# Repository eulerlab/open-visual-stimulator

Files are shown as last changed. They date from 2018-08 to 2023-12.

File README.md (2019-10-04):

## Open Visual Stimulator

This repository holds the resources for a flexible, spatial visual stimulator with up to 6 chromatic channels. It combines commercial digital light processing (DLP) devices with open hard- and software components that can be easily adapted to the experimentalist’s specific needs. With this we intend to start a community effort of sharing and further developing a common stimulator design.

Please find more details on the stimulator in the following publication:

_Franke K*, Maia Chagas A*, Zhao Z, Zimmermann MJY, Bartel P, Qiu Y, Szatko K, Baden T, Euler T# (2019). An arbitrary-spectrum spatial visual stimulator for vision research. eLife 2019;8:e48779, [10.7554/eLife.48779](https://elifesciences.org/articles/48779)._

For the newest changes and additions, see [release notes](https://github.com/eulerlab/open-visual-stimulator/blob/master/release_notes.md)

### Pictures

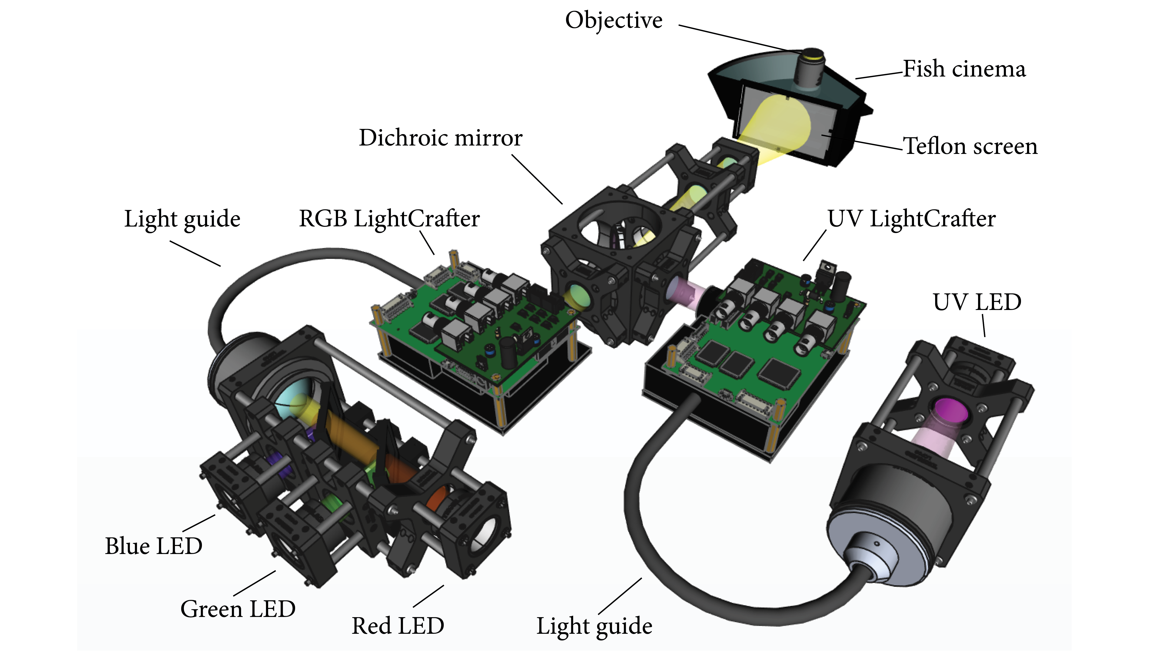
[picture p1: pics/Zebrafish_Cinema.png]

_Rendering of the 4-channel R-G-B-UV zebrafish stimulator (by MJY Zimmermann)._

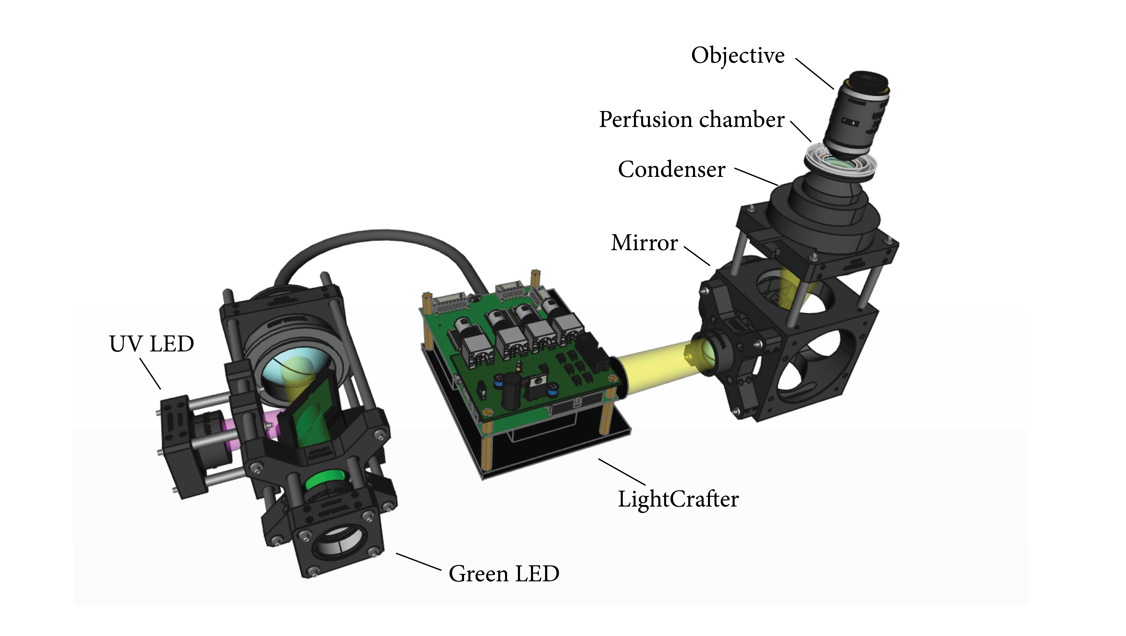
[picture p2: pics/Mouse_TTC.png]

_Rendering of through-the-conderser (TTC) G-UV mouse light stimulator (by MJY Zimmermann)._

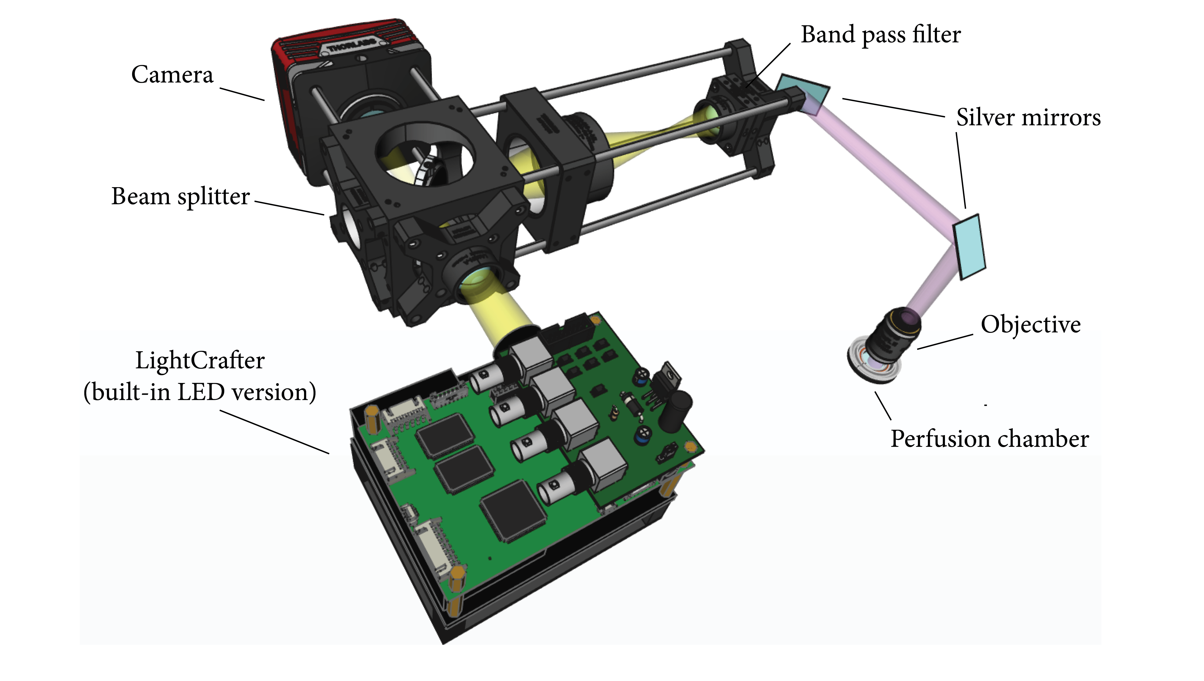
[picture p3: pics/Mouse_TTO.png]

_Rendering of through-the-objective (TTO) G-UV mouse light stimulator (by MJY Zimmermann)._ 

### Ordering of PCB boards

If you are interested in ordering boards and components, please find more information in the boards folder [readme](https://github.com/eulerlab/open-visual-stimulator/blob/master/boards/readme.md) file.

## Repository structure

```
├───pics                                      Pictures
├───boards                                    LED driver/blanking boards
│   ├───lcr_add-on                            - KiCad files for board that combines LCr and
|   |   |                                       blanking signals
|   |   ├───connector_coaxial.pretty          - BNC connector description (KiCad)
|   |   └───gerber                            - Gerber files for circuit board
│   ├───mosfet_circuit                        - KiCad files for board that switches switch LEDs
|   |   ├───connector_coaxial.pretty          - BNC connector description (KiCad)
|   |   └───gerber                            - Gerber files for circuit board
|   ├───mosfet_circuit_plus_voltage_regulator - KiCad files for board that combines voltage
|   |   |                                       regulator and LED switching
|   |   ├───connector_coaxial.pretty          - BNC connector description (KiCad)
|   |   └───gerbers                           - Gerber files for circuit board
|   ├───ssr_board                             - KiCad files for solid state relay board
|   |   └───gerbers                           - Gerber files for circuit board
|   └───arduino_code_for_testing_circuits     - Arduino code to emulate blanking and LCr signals
|       └───lcr_emulator
|
├───printed_parts                             OpenSCAD and STL files for 3D printed parts
|   |
│   ├───Fish_cinema                           - Fish tank used in the fish setup
│   ├───SSR_board                             - Designs for plate and cover of the SSR board
│   └───optical_components                    - optomechanical parts for LED assemblies
|           ├───fish_stimulator
|           ├───cmouse_stimulator
|           └───lcr_addons
├───calibration_mouse                         Calibration of dichroic mouse stimulator
│   ├───data                                  - recorded calibration data (custom LEDs and TFT monitor)
│   ├───datasheets                            - spectrometer data sheet, etc.
│   ├───filters                               - dichroic filter spectra
│   ├───light-sources                         - spectra of LEDs
│   ├───opsins                                - mouse opsin sensitivity curves
│   ├───scripts                               - Python scripts used in iPython notebooks
|   └───spectrometer-calibration-files        - USB2+ calibration data
|
└───calibration_zebrafish                     Calibration of tetrachromatic zebrafish stimulator
    ├───data                                  - recorded calibration data (custom LEDs)
    ├───datasheets                            - spectrometer & powermeter data sheet.
    ├───light-sources                         - LED spectra measured behind the teflon screen
    ├───opsins                                - zebrafish opsin sensitivity curves
    └───scripts                               - Python scripts used in iPython notebooks
```

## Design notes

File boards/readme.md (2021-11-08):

## LED driver/blanking boards

LED blanking circuits were inspired by earlier devices designed and built by R. Berndt (HIH Tübingen).

`lcr_add-on` - KiCad and Gerber files for the "logic board". This board combines the signals from the LCr with an external "blanking signal" to independently control up to three 3 LEDs per lightcrafter device. This board has a jumper option to disable the blanking signal altogether, which may be useful when e.g. using LCrs in MEA setups.

`mosfet_circuit` - KiCad and Gerber files for "LED driver board". This board uses the 5V logic signal from Lcr_addon ("logic board") to turn LEDs on and off. Users need to connect this board to an appropriate power suply (i.e. a power supply the is outputing the LED forward voltage).

`mosfet_circuit_plus_voltage_regulator` - KiCad and Gerber files for "LED driver board". This board uses the 5V logic signal from Lcr_addon ("logic board") to turn LEDs on and off. This board has a stepdown voltage regulator built-in. It is capable of 20V and 1.5A max output with the components present in its "1-click-bom.csv" file. (see "Components to populate the boards" for more details).

`ssr_board` - This board controls the LED power lines from the Lightcrafter by opening and closing them using solid state relays. The relays are controlled by a 5V signal (in this case the inverted blanking signal).

### General information about the printed circuit boards:

- For details on the design and function of the boards, see [preprint](https://www.biorxiv.org/content/10.1101/649566v1)).

- The boards were designed using [KiCad 5](http://www.kicad.org/) and can be ordered using the `Gerber.zip` file located in each board's `gerber` subfolder.

- Several "board on demand" companies are available, and the process of ordering is pretty much the same. A more detailed tutorial on how to do so can be found [here](https://www.youtube.com/watch?v=ENmDnoKs2hM) (for simply using the already available compressed files, go to minute 7 of the video).

- Companies providing "board on demand" service include:

   - [JLCPCB](https://jlcpcb.com/)
   - [PCBWAY](https://www.pcbway.com)
   - [OSH PARK](https://oshpark.com/)
   - [AISLER](https://aisler.net/)

### Components to populate the boards:

Components are listed on each board folder on a "comma separated value" file named `1-click-bom.csv`. Listed in the file are the quantity, identification and supplier of each component. They can also be ordered using [KitSpace](kitspace.org):

 - [LCr_addon on kitspace](https://kitspace.org/boards/github.com/eulerlab/open-visual-stimulator/boards/lcr_add-on/)
 - [mosfet circuit on kitspace](https://kitspace.org/boards/github.com/eulerlab/open-visual-stimulator/boards/mosfet_circuit/)
 - [mosfet  plus voltage regulator circuit on kitspace](https://kitspace.org/boards/github.com/eulerlab/open-visual-stimulator/boards/mosfet_circuit_plus_voltage_regulator/)

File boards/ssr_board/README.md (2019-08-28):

# Open Visual Stimulator - Solid State relay board

This board controls the LED power lines from the Lightcrafter by opening and closing them using solid state relays. The relays are controlled by a 5V signal (in this case the inverted blanking signal).

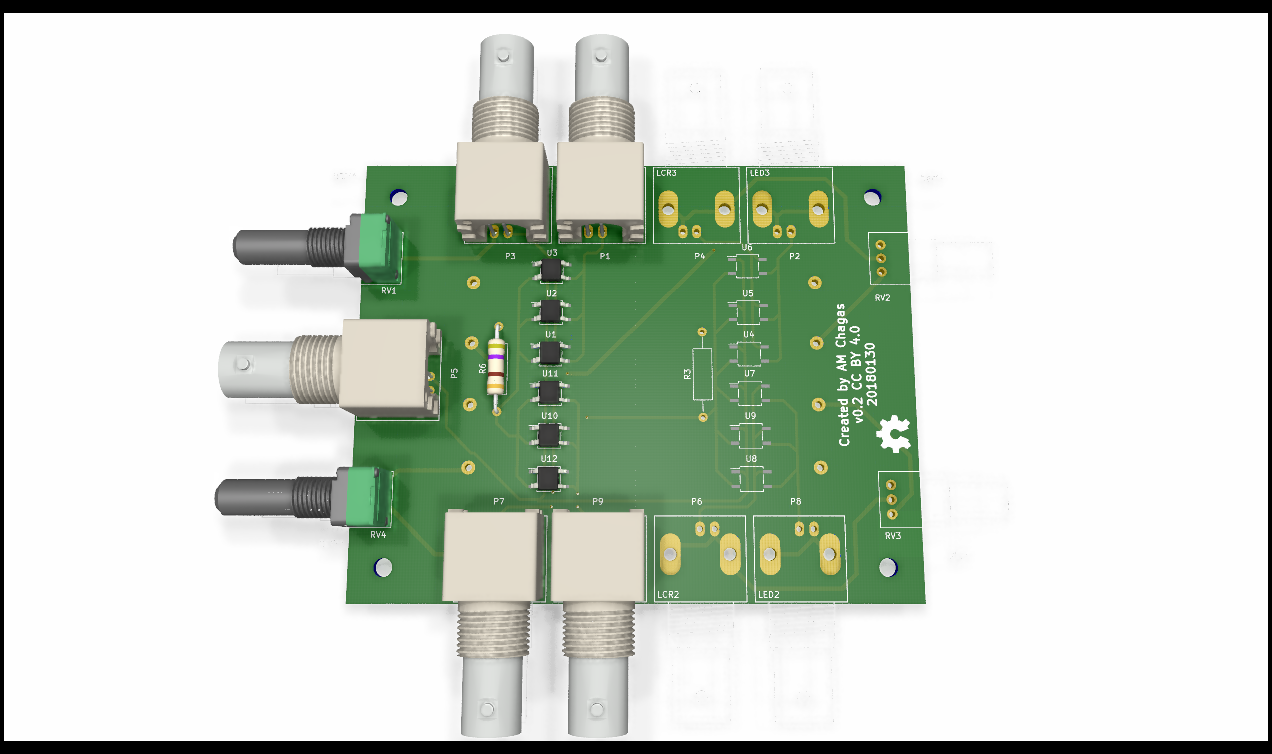
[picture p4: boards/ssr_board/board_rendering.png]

rendering for two out of four possible channels.

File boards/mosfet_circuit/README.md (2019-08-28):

# Open Visual Stimulator - MOSFET Circuit PCB

A board ("LED driver board") for fast switching LEDs on/off, part of the Open Source visual stimulator project.

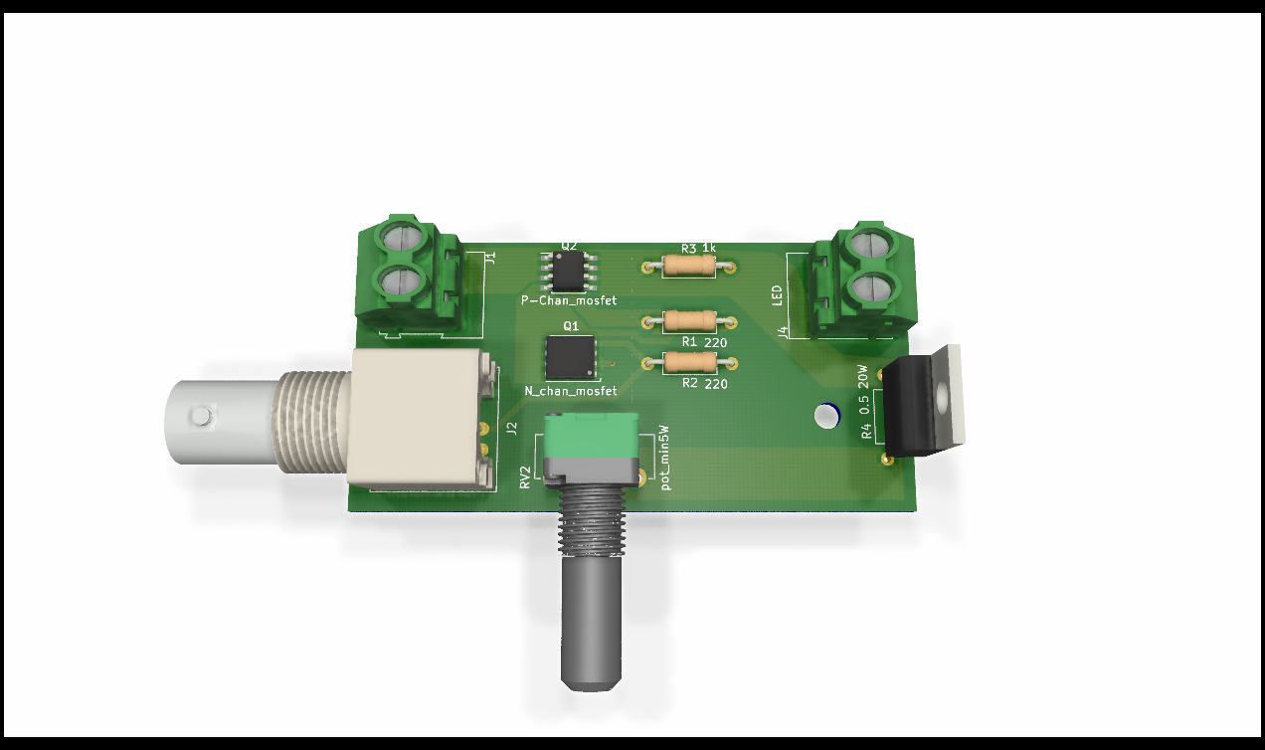
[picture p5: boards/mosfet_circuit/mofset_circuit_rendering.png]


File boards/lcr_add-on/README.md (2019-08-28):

# Open Visual Stimulator - LCR add-on PCB

A board for integrating signals from a lightcrafter to a 2P microscope ("logic board"), part of the Open source visual stimulator project.

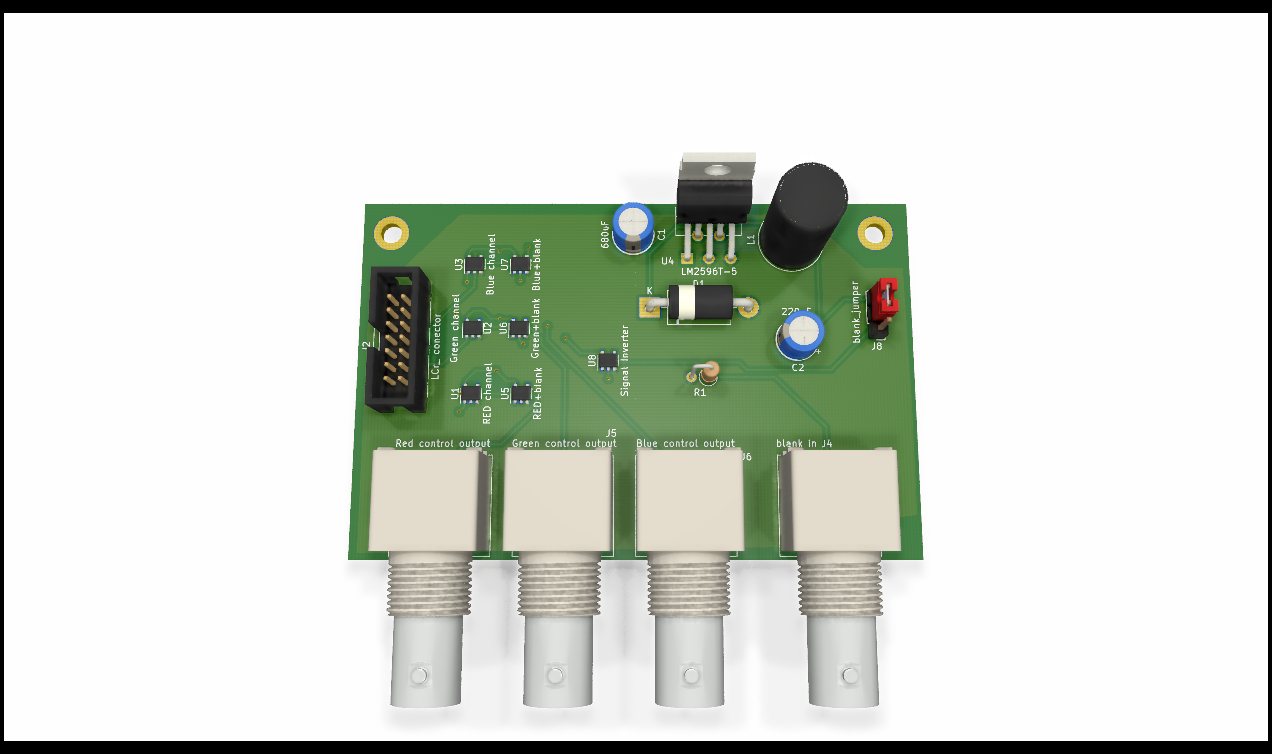
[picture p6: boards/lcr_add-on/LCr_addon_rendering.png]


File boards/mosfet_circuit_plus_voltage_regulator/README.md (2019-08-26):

# Open Visual Stimulator - mosfet circuit plus voltage regulator

A board that contains a voltage regulator and a fast switching (tens of microsseconds) circuit for turning LEDs on and off

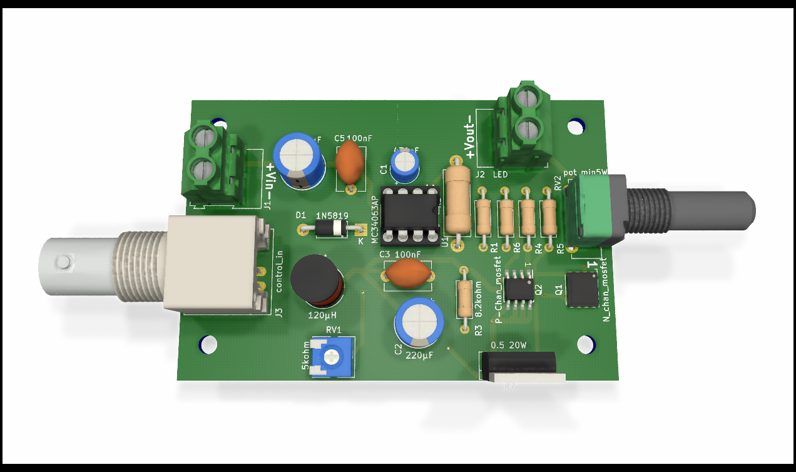
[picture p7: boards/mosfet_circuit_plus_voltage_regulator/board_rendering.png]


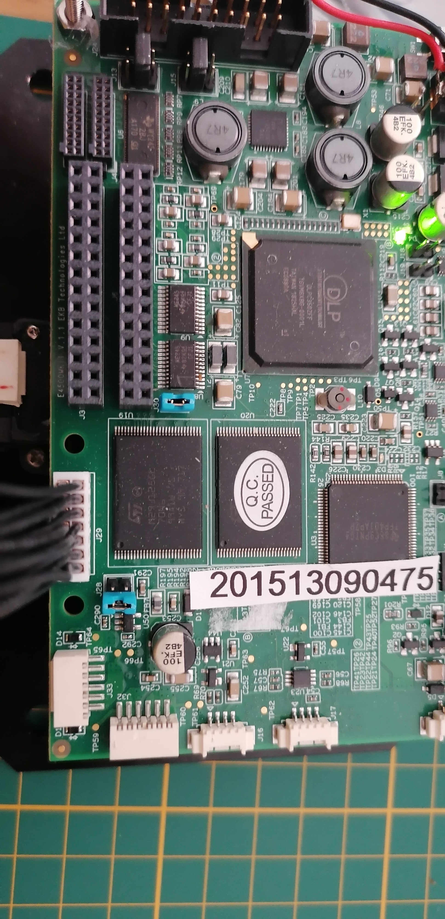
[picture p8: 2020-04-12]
pics/LCr_jumpers.jpg

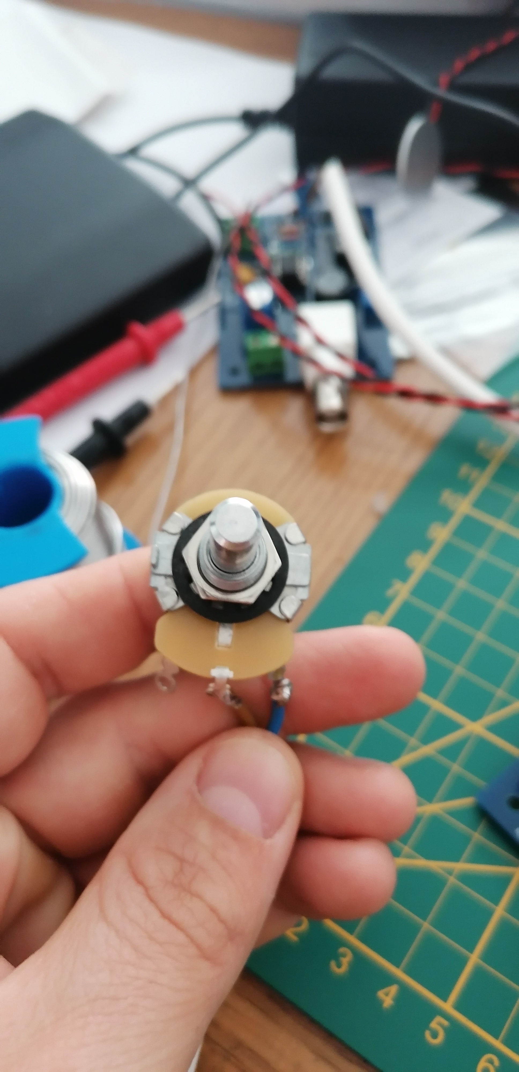
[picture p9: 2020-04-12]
pics/potentiometer.jpg

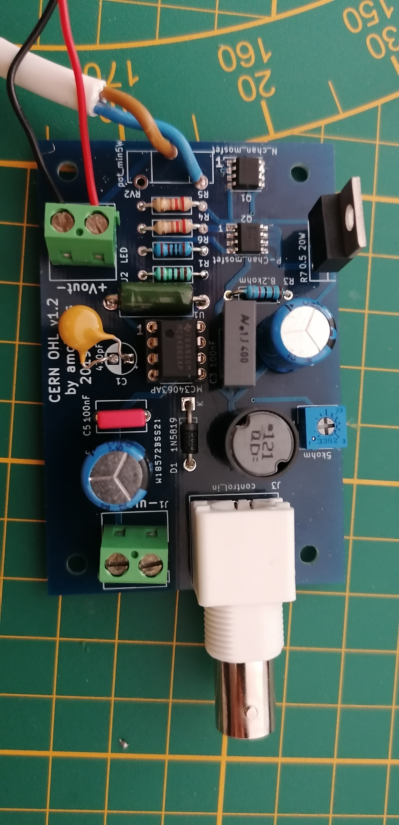
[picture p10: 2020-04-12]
pics/mosfet_plus_voltage_supply.jpg

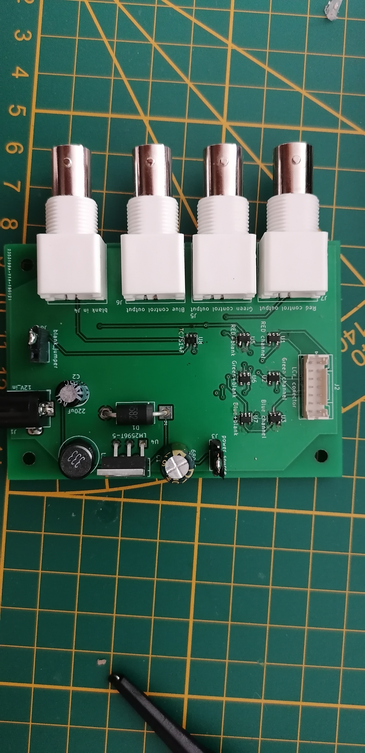
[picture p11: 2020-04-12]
pics/LCr_add_on.jpg

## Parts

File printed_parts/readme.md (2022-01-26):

## 3D printed parts

OpenSCAD (`.scad`) and STL (`.stl`) files for various optomechanical components.

- `SSR_board` contains the designs for parts to hold the board.
- `Fish_cinema` contains the designs for the fish tank that is placed under the objective in the fish stimulator.
- `Optical components` contains the following folders:
  - [mouse stimulator](./optical_components/mouse_stimulator), contains designs used in the LED assembly.
  - [fish stimulator](./optical_components/fish_stimulator), contains designs used in the LED assembly.
  - [lightcrafters](./optical_components/lcr_addons), contains parts that can be printed to modify the LCrs.
  - [ND_filterholder](./optical_components/ND_filterholder) contains file for a design that hold ND filters from Thorlabs and easily fits on their cage system.

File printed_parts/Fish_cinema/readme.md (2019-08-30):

## 3D printed parts

OpenSCAD and STL files for fish "cinema".

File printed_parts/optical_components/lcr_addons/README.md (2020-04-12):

## In this section, users will find files to make additions/modifications to the lightcrafter

 - `fibre_coupler` - The folder contains files for a part that can be used to couple Thorlabs [light fibre](https://www.thorlabs.com/thorproduct.cfm?partnumber=LLG05-4H) to one of the LEDs ports on side of the lightcrafter. This was created by David Ide (ided[at]mail.nih.gov), Biomedical Engineering Technician, NIMH Section on Instrumentation. 

 - `LCr_tilter` - The folder contains files describing two parallel plates that when fixed below the LCr can be used it to tilt it downwards, to compensate for the device's upward projection.

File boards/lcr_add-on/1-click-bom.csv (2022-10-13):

References | Qty | Description | Manufacturer | MPN | Manufacturer_1 | MPN_2 | Manufacturer_3 | MPN_4 | Manufacturer_5 | MPN_6 | Manufacturer_7 | MPN_8 | Digikey | Mouser | RS | Newark | Farnell
U4; | 1 | LM2596 5v | ITO-220 | Texas Instruments | Texas Instruments | LM2596T-5.0/NOPB |  |  |  |  |  |  | LM2596T-5.0/NOPB-ND | 926LM2596T5.0/NOPB | 5333743 | 97K3256 | 1150103
L1; | 1 | INDUCTOR 33µH Neosid MA-Bs75 | Bourns | RLB0914-330KL |  |  |  |  |  |  |  |  | RLB0914-330KL-ND | 652RLB0914330KL | 8118853 | 61J7916 | 2309242
D1; | 1 | Diode Schottky 5A DO-201AD | Vishay | 1N5822-E3/73 | Zetex | SB5100-T |  |  |  |  |  |  | 1N5822-E3/73GICT-ND | 6251N5822E3/73 | 751-4843 | 17T8202 | 1336553
C2; | 1 | CAP ALUM 220UF 20% 25V RADIAL | Panasonic | EEU-FM1E221 | Panasonic | ECA-1CM221B | Panasonic | ECE-A0GKS221 | Panasonic | EEU-EB1A221S |  |  | P12383-ND | 667ECA1CM221B | 7472036 | 70K9673 | 9451099
C1; | 1 | 680µF Capacitor | Rubycon | 16ZL680MEFC10X16 | Panasonic | EEU-FC1A681 |  |  |  |  |  |  | 1189-3978-ND | 667EEUFC1A681 | 7037258 | 31M6417 | 1144691
R1; | 1 | Resistor 1k 250mW through-hole | Multicomp | MF12 1K | Yageo | MFR-25FBF52-1K | RS Pro | 7077666 |  |  |  |  | 1.00KXBK-ND | 603MFR25FBF521K | 7077666 | 38K5400 | 9342400
J2; | 1 | Lcr connector | JST | B14B-PHDSS(LF)(SN) |  |  |  |  |  |  |  |  | 455-1764-ND |  | 918-2738
J4;J5;J6;J7; | 4 | BNC connector | TE | 1-1337542-0 |  |  |  |  |  |  |  |  | A97552-ND |  | 512-1203
J8; | 1 | jumper connector | SamTec | SSW-103-01-G-S |  |  |  |  |  |  |  |  | SAM1209-03-ND |  | 765-5610
U1;U2; | 2 | SN74LS08N AND gate array | TI | SN74LS08N |  |  |  |  |  |  |  |  | 296-1633-5-ND
U3; | 1 | SN74HC14N Signal inverter (NOT gate) array | TI | SN74HC14N |  |  |  |  |  |  |  |  | 296-1577-5-ND |  | 540-6885
Lcr 1 | 2 | Female plug 2X14 (1 to Lcr one to Board) | JST | PHDR-14VS |  |  |  |  |  |  |  |  | 455-1172-ND |  | 917-4692 | 917-4692
Cable | 14 | JUMPER SPHD-001T-P0.5 X2 10 | JST | APAPA22K254 |  |  |  |  |  |  |  |  | 455-3357-ND

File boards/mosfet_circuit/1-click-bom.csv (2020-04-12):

References | Qty | Description | Manufacturer | MPN | Manufacturer_1 | MPN_2 | Manufacturer_3 | MPN_4 | Manufacturer_5 | MPN_6 | Manufacturer_7 | MPN_8 | Digikey | Mouser | RS | Newark | Farnell
Q2 | 1 | P-Channel MOSFET | Fairchild | FDS6575 |  |  |  |  |  |  |  |  | FDS6575CT-ND |  | 671-0570
Q1 | 1 | N-Channel mosfet | Vishay | SI4840BDY-T1-GE3 |  |  |  |  |  |  |  |  | SI4840BDY-T1-E3CT-ND |  | 710-4736
R1;R2 | 2 | Resistor 220 ohm 250mW through-hole | Yageo | MFR-25FBF52-220R | TE Connectivity | CBT25J220R | TE Connectivity | CFR16J220R | Ohmite | OD221JE | Stackpole Electronics | CF14JT220R | CF14JT220RCT-ND | 279CBT25J220R | 8066376 | 21R0186 | 1265068
R3 | 1 | Resistor 1k 250mW through-hole | Multicomp | MF12 1K | Yageo | MFR-25FBF52-1K | RS Pro | 7077666 |  |  |  |  | 1.00KXBK-ND | 603MFR25FBF521K | 7077666 | 38K5400 | 9342400
R4; | 1 | Resistor 20W TO-220 | Bourns | PWR220T-20-R500F |  |  |  |  |  |  |  |  | PWR220T-20-R500F-ND | 652PWR220T20R500F | 7962508 | 55R1098 | 2328267
J1;J4 | 2 | Terminal block 5mm | RS Pro | 494-8906 | TE Connectivity | 282837-2 |  |  |  |  |  |  | A113320-ND |  | 494-8906
RV2 | 1 | Potentiometer 25Ohms 5W | CTS | 026TB32R250B1A1 |  |  |  |  |  |  |  |  | CT2152-ND |  | 179-0668
J2 | 1 | BNC connector | TE | 1-1337542-0 |  |  |  |  |  |  |  |  | A97552-ND |  | 512-1203

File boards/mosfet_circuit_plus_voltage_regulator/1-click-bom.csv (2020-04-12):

References | Qty | Description | Manufacturer | MPN | Manufacturer_1 | MPN_2 | Manufacturer_3 | MPN_4 | Manufacturer_5 | MPN_6 | Manufacturer_7 | MPN_8 | Digikey | Mouser | RS | Newark | Farnell
Q2 | 1 | P-Channel MOSFET | Fairchild | FDS6575 |  |  |  |  |  |  |  |  | FDS6575CT-ND |  | 671-0570
Q1 | 1 | N-Channel mosfet | Vishay | SI4840BDY-T1-GE3 |  |  |  |  |  |  |  |  | SI4840BDY-T1-E3CT-ND |  | 710-4736
R1 | 1 | 1.5kohm | TE Connectivity | LR1F1K5 |  |  |  |  |  |  |  |  | A105952CT-ND |  | 148-540
R2 | 1 | 0.22ohm | Vishay | RWM0410R220JR15E1 |  |  |  |  |  |  |  |  | RWMA-.22CT-ND |  | 485-1414
R3 | 1 | 8.2kohm | TE Connectivity | LR1F8K2 | Vishay | MRS25000C8201FCT00 |  |  |  |  |  |  | BC4264CT-ND |  | 148-714
R4;R5 | 2 | Resistor 220 ohm 250mW through-hole | Yageo | MFR-25FBF52-220R | TE Connectivity | CBT25J220R | TE Connectivity | CFR16J220R | Ohmite | OD221JE | Stackpole Electronics | CF14JT220R | CF14JT220RCT-ND | 279CBT25J220R | 8066376 | 21R0186 | 1265068
R6 | 1 | Resistor 1k 250mW through-hole | Multicomp | MF12 1K | Yageo | MFR-25FBF52-1K | RS Pro | 7077666 |  |  |  |  | 1.00KXBK-ND | 603MFR25FBF521K | 7077666 | 38K5400 | 9342400
R7 | 1 | Resistor 20W TO-220 | Bourns | PWR220T-20-R500F |  |  |  |  |  |  |  |  | PWR220T-20-R500F-ND | 652PWR220T20R500F | 7962508 | 55R1098 | 2328267
J1;J2 | 2 | Terminal block 5mm | RS Pro | 494-8956 | TE Connectivity | 282836-2 | TE Connectivity | 282837-2 |  |  |  |  | A113320-ND |  | 494-8956
J3 | 1 | BNC connector | TE | 1-1337542-0 |  |  |  |  |  |  |  |  | A97552-ND |  | 512-1203
RV1 | 1 | 5kohm | Bourns | 3362P-1-502LF |  |  |  |  |  |  |  |  | 3362P-502LF-ND |  | 522-0978
RV2 | 1 | Potentiometer 25Ohms 5W | CTS | 026TB32R250B1A1 |  |  |  |  |  |  |  |  | CT2152-ND |  | 179-0668
D1 | 1 | 1N5819 diode | ON | 1N5819G |  |  |  |  |  |  |  |  | 1N5819GOS-ND |  | 774-3347
C1 | 1 | 470pF capacitor | Vishay | 562R10TST47 |  |  |  |  |  |  |  |  | 562R10TST47-ND |  | 831-3023
C2;C4 | 1 | 220µF capacitor (line filter) | Vishay | MAL214650221E3 |  |  |  |  |  |  |  |  | 4485PHBK-ND |  | 684-1725
C3;C5 | 2 | 100nF capacitor (line filter) | Wima | MKS2D031001A00KI00 | TDK | FG26C0G1H104JNT06 |  |  |  |  |  |  | 445-173396-1-ND |  | 108-2700
L1 | 1 | 120µH inductor | Panasonic | ELC11D121F | Bourns | RL622-121K-RC |  |  |  |  |  |  | M9994-ND |  | 675-5400
U1 | 1 | MC34063AP step up/down regulator | texas instruments | MC34063AP |  |  |  |  |  |  |  |  | 296-17766-5-ND |  | 661-8430
U1-1 | 1 | DIP-8 socket | Preci-dip | 110-87-308-41-001101 | Assmann | A 08-LC-TT |  |  |  |  |  |  | AE9986-ND |  | 674-2435

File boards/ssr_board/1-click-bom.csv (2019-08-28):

References | Qty | Description | Manufacturer | MPN | Manufacturer_1 | MPN_2 | Manufacturer_3 | MPN_4 | Manufacturer_5 | MPN_6 | Manufacturer_7 | MPN_8 | Digikey | Mouser | RS | Newark | Farnell
P1-9 | 9 | BNC connector | TE | 1-1337542-0 |  |  |  |  |  |  |  |  |  |  | 512-1203
R3;R6 | 2 | Resistor 1k 250mW through-hole | Multicomp | MF12 1K | Yageo | MFR-25FBF52-1K | RS Pro | 7077666 |  |  |  |  | 1.00KXBK-ND | 603MFR25FBF521K | 7077666 | 38K5400 | 9342400
RV1-4 | 4 | Potentiometer 25Ohms 5W | CTS | 026TB32R250B1A1 |  |  |  |  |  |  |  |  |  |  | 179-0668
U1-12 | 12 | Optocoupler 250mA max current | Panasonic | AQY221R2S |  |  |  |  |  |  |  |  |  |  | 699-6610
R1;R2;R4;R5 | 4 | 2 Ohm 5W resistor | Vishay | RS0052R000FE12 |  |  |  |  |  |  |  |  |  |  | 850-6613

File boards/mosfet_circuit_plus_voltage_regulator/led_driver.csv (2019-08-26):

Source: | /home/andre/Documents/repositories/amchagas/open-visual-stimulator/boards/mosfet_circuit_plus_voltage_regulator/led_driver.sch
Date: | Fri 19 Jul 2019 14:24:53 BST
Tool: | Eeschema 5.0.2-bee76a0~70~ubuntu18.04.1
Component Count: | 26
Ref | Value | Footprint | Datasheet | Manufacturer | Vendor
C1 | 470pF | Capacitor_THT:CP_Radial_D5.0mm_P2.50mm | ~
C2 | 220µF | Capacitor_THT:CP_Radial_D8.0mm_P5.00mm | ~
C3 | 100nF | Capacitor_THT:C_Disc_D8.0mm_W5.0mm_P7.50mm | ~
C4 | 220µF | Capacitor_THT:CP_Radial_D8.0mm_P5.00mm | ~
C5 | 100nF | Capacitor_THT:C_Disc_D8.0mm_W5.0mm_P7.50mm | ~
D1 | 1N5819 | Diode_THT:D_DO-41_SOD81_P10.16mm_Horizontal | http://www.vishay.com/docs/88525/1n5817.pdf
H1 | MountingHole | MountingHole:MountingHole_3.2mm_M3 | ~
H2 | MountingHole | MountingHole:MountingHole_3.2mm_M3 | ~
H3 | MountingHole | MountingHole:MountingHole_3.2mm_M3 | ~
H4 | MountingHole | MountingHole:MountingHole_3.2mm_M3 | ~
J1 | Vin | TerminalBlock:TerminalBlock_Altech_AK300-2_P5.00mm | ~
J2 | LED | TerminalBlock:TerminalBlock_Altech_AK300-2_P5.00mm | ~
J3 | control_in | Connector_Coaxial_extra:BNC_Amphenol_B6252HB-NPP3G-50_Horizontal | ~
L1 | 120µH | Inductor_THT:L_Radial_D7.5mm_P5.00mm_Fastron_07P | ~
Q1 | N_chan_mosfet | Package_TO_SOT_SMD:TDSON-8-1 | http://www.ti.com/lit/gpn/csd17577q5a
Q2 | P-Chan_mosfet | Package_SO:SOIC-8_3.9x4.9mm_P1.27mm | http://www.infineon.com/dgdl/irf7404.pdf?fileId=5546d462533600a4015355fa2b5b1b9e
R1 | 1.5kohm | Resistor_THT:R_Axial_DIN0207_L6.3mm_D2.5mm_P10.16mm_Horizontal | ~
R2 | 0.22ohm | Resistor_THT:R_Axial_DIN0414_L11.9mm_D4.5mm_P15.24mm_Horizontal | ~
R3 | 8.2kohm | Resistor_THT:R_Axial_DIN0207_L6.3mm_D2.5mm_P10.16mm_Horizontal | ~
R4 | 220 | Resistor_THT:R_Axial_DIN0207_L6.3mm_D2.5mm_P10.16mm_Horizontal | ~
R5 | 220 | Resistor_THT:R_Axial_DIN0207_L6.3mm_D2.5mm_P10.16mm_Horizontal | ~
R6 | 1k | Resistor_THT:R_Axial_DIN0207_L6.3mm_D2.5mm_P10.16mm_Horizontal | ~
R7 | 0.5 20W | Package_TO_SOT_THT:TO-220-2_Vertical | ~
RV1 | 5kohm | Potentiometer_THT:Potentiometer_Vishay_T73YP_Vertical | ~
RV2 | pot_min5W | Potentiometer_THT:Potentiometer_ACP_CA14-H5_Horizontal | ~
U1 | MC34063AP | Package_DIP:DIP-8_W7.62mm | http://www.onsemi.com/pub_link/Collateral/MC34063A-D.PDF

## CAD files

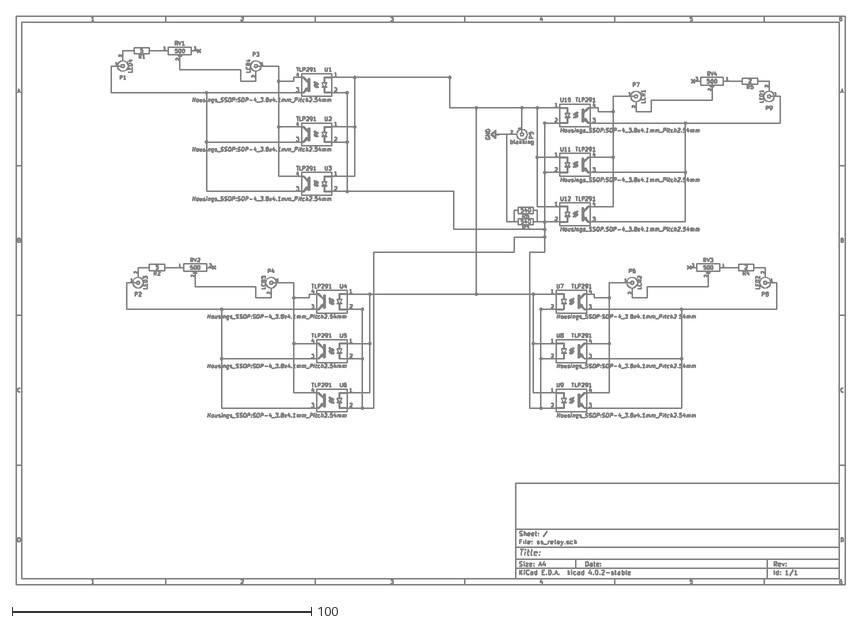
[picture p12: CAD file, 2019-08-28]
boards/ssr_board/ss_relay.dxf
277.0 x 190.0

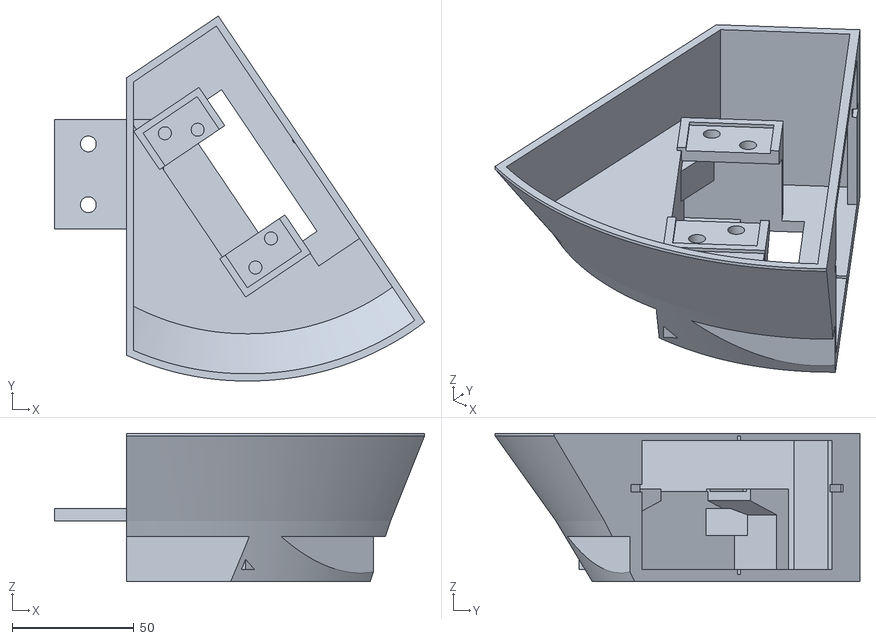
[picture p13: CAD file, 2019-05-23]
printed_parts/Fish_cinema/Fish Cinema v10.0_40X_Objective.stl
152.3 x 150.1 x 61.0

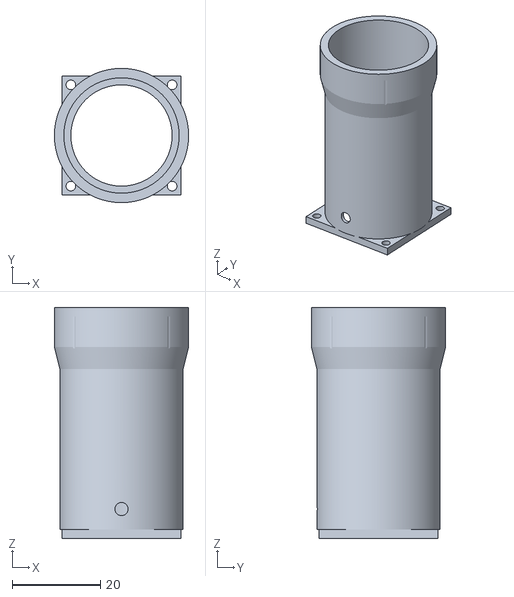
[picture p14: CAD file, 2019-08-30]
printed_parts/optical_components/fish_stimulator/DMD_lens_adapter.stl
30.5 x 30.5 x 52.5

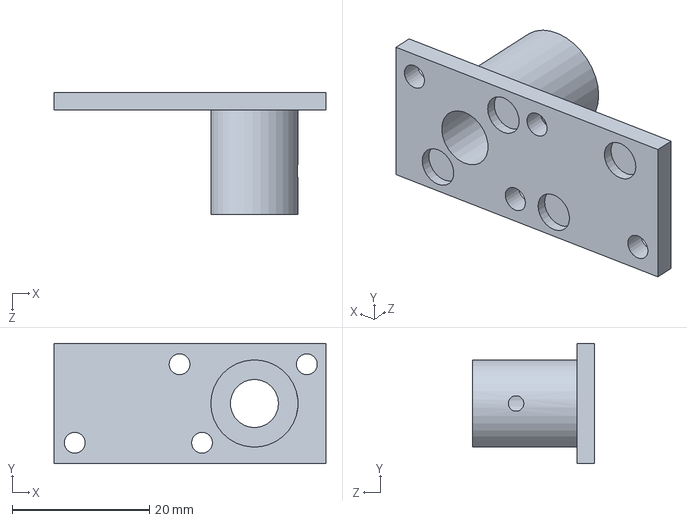
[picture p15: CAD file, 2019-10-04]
printed_parts/optical_components/lcr_addons/fibre_coupler/light guide holder.SLDPRT
39.6 x 17.5 x 17.8 mm

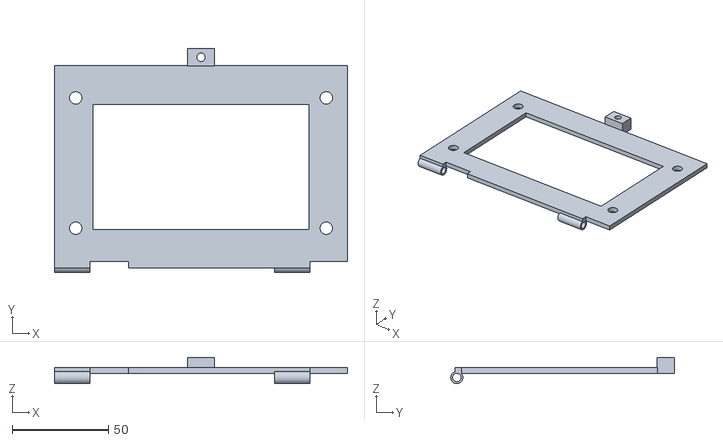
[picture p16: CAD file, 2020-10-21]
printed_parts/optical_components/lcr_addons/LCr_tilter/Lcr_tilter_plate1.stl
152.0 x 116.0 x 13.7

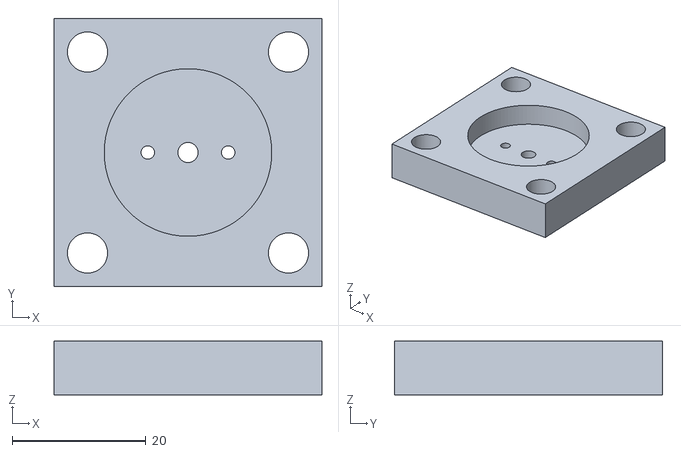
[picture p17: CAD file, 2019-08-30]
printed_parts/optical_components/mouse_stimulator/LED_holder_plate.stl
40.0 x 40.0 x 8.00

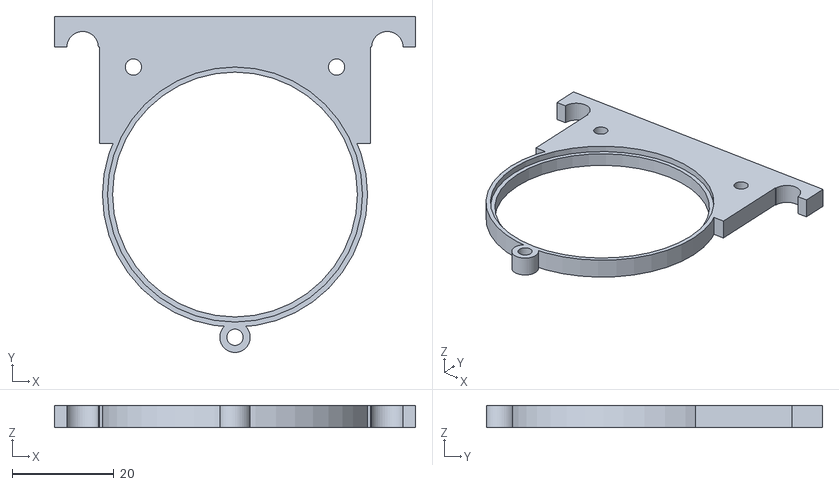
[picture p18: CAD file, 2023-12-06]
printed_parts/optical_components/ND_filter_holder/ND_filterholder_rigid_plastic.stl
71.1 x 66.1 x 4.39

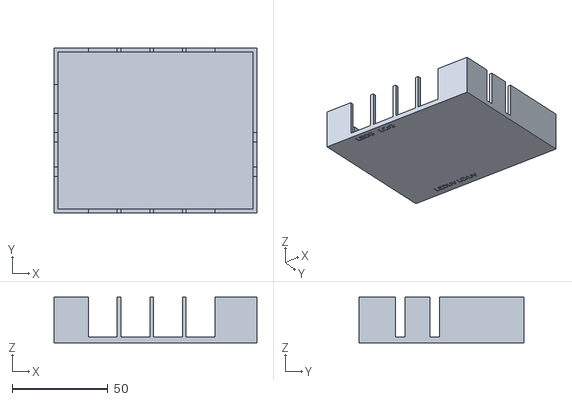
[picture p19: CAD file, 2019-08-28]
printed_parts/SSR_board/pcb_case_top.stl
106.0 x 86.0 x 24.0

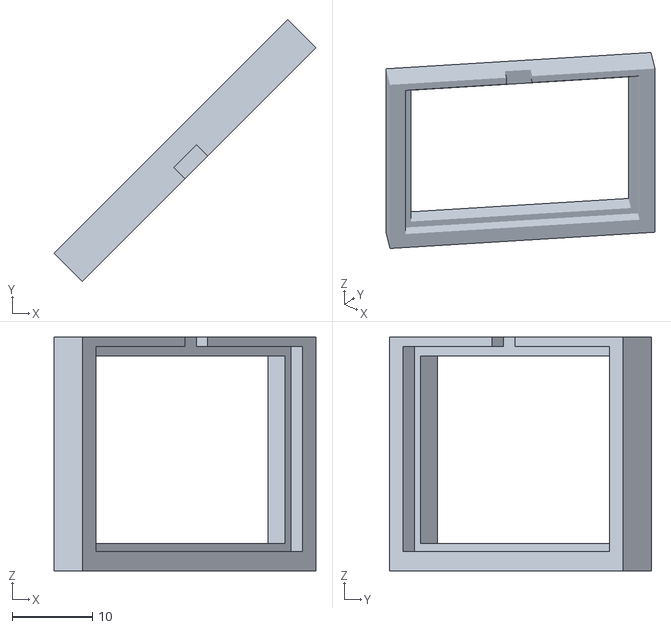
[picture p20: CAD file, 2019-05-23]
printed_parts/optical_components/fish_stimulator/dichroic_frame.stl
32.7 x 32.7 x 29.1

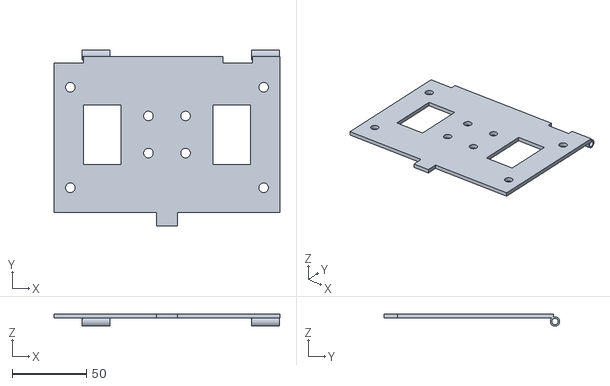
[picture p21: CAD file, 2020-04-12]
printed_parts/optical_components/lcr_addons/LCr_tilter/Lcr_tilter_plate2.stl
152.0 x 118.0 x 8.40

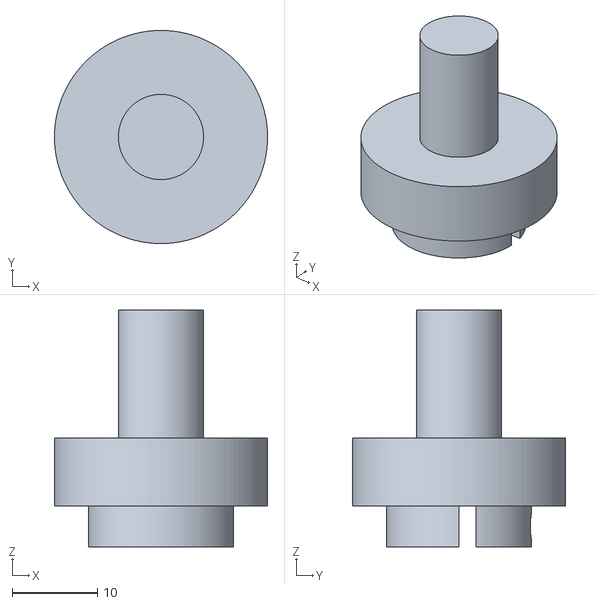
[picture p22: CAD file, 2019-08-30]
printed_parts/optical_components/mouse_stimulator/mirror_holder.stl
25.0 x 25.0 x 27.8

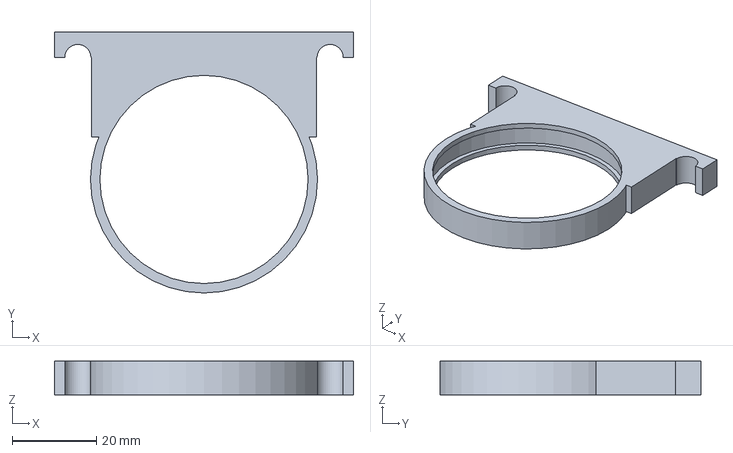
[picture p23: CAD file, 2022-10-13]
printed_parts/optical_components/ND_filter_holder/ND_filterholder_5mm_thick_filter.3mf
71.1 x 62.0 x 8.00 mm

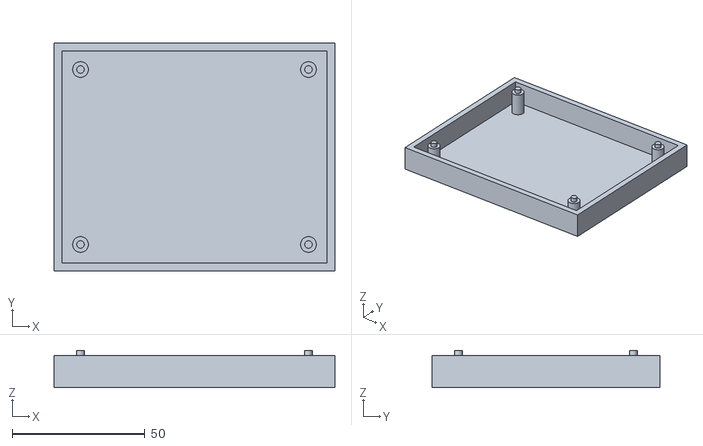
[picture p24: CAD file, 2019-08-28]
printed_parts/SSR_board/pcb_case_bottom.stl
106.0 x 86.0 x 14.0

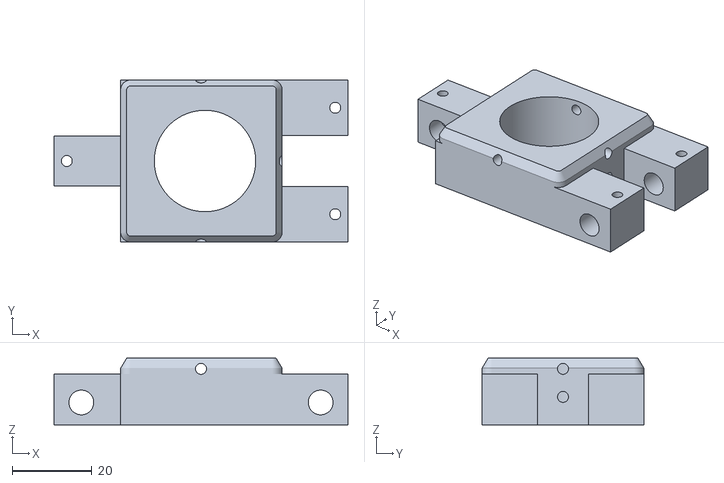
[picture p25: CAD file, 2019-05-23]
printed_parts/optical_components/fish_stimulator/LCP30 - modified.stl
73.7 x 40.6 x 16.7

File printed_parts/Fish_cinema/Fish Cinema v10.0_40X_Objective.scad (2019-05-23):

// Fish Cinema v10.0
// Designed by Bartel & Zimmermann, BadenLab, University of Sussex
// Modified on 20190305 by AM Chagas
// CC BY SA 4.0
// 

    // // // // // // // // // //  // // // // // //
   // // // // // Variables for Users// // // // //
  // // // // // // // // // // //  // // // // //
  

              Smoothness = 360; //  
              tol = 0.125; // Tolerance applied to the seal tight
              Walls = 3; // Thickness of tank walls
              sep = 0 ; //z_separation for mount() and slide()
              rotation = 34; //Angle of the screen relative to the y_axis in degrees (0-85° ; 270-360°)
              Format = 16/9; //Screen resolution (16/9, 4/3, 5/4, etc.)


               d_Screen = 33.5/2+10; //Screen distance from the fish lens (33.5=R_Objective)
               FoV_angle = 128/2; // Field of View angle: 128 immuno file, 165 described
               visual_angle = 1; // Larvae visual resolution 
               objective_angle = 36; // Maximum angle with objective hindrance
               tt=360;
    
    // // // // // // // // // // // // 
   // // // // Switches // // // // //
  // // // // // // // // // // // //
    reference = 0;
               Holder = 1;
               Tank = 1;
               Screen = 0;
               
                        Objective = 0;
                        FieldOfView = 0;
                        FieldOfView_Limits=0;
                        Screen2 = 0;
                        Fish = 0;

  // // // // // // // // // // // // // // // // // // // // // // // //
 // // // // // // // // // // // // // // // // // // // // // // // //
// // // // // // // // // // // // // // // // // // // // // // // //

//translate([-100,-100,Bottom+h_Screen/2-z_Glass+2*tol+tol])cube([200,200,tol]);

//Holder parameters
    x_Holder = 45;
    y_Holder = 45;
    z_Holder = 5;
    x_HolderPos = -80;
    y_HolderPos = -y_Holder/2;
    z_HolderPos = 25;
    x_ScrewPos = x_HolderPos+14;
    y_ScrewPos = 10;
    z_ScrewPos = z_HolderPos;
    Screw_M6 = 6.5/2; //hole for M6 screws
    pos_x_Holder_Support = x_HolderPos+x_Holder-15.4;

//Tank parameters
    z_Bottom = 1.5;
    Bottom = z_Bottom + 3.5;
    h_Tank = 60; //height of the tank
    r1 = 80; //radius of the first level (bottom of the tank)
    r2 = r1 + 15; //radius of the second level
    r3 =  r2 + 25; //radius of the third level (top of the tank)
    h_r1_r2 = z_HolderPos; //first level height
    h_r2_r3 = h_Tank - h_r1_r2; //second level height
    x_Tank = 1;
    y_Tank = 40;
    z_Tank = 1;
    r_Rubber = 25/2; //rubber seal radius 
    z_Rubber = 1; //rubber seal thickness
    y_Minkowski = 75;// Modify the length of the tank
    Margin = 20; //back wall y position relative to the origin + x_Holder

//Mount parameters
    SealHole = 40/2;
    MainHole = 20/2;
    h_Mount = h_Tank/2;
    GlassRing = 25/2;
    r_Seal = 35/2;
    Seal_Width = 2;
    h_Seal =(Bottom-z_Bottom)/2;

//Slide Holder parameters
    x_Slide = 26;
    z_Slide = 4.5;
    x_Glass = 22;

//Screen parameters
    h_Screen = h_Tank-Bottom+1-Walls;
    
// Glass Slide
x_Glass = 25.85 + 4*tol;
y_Glass = 75.75 + 4*tol;
z_Glass = 1.0;

//Magnet
r_Magnet = 5.1/2;
y_Magnet = 19;
h_Magnet = 3.1;


    
    
// Objective parameters
R_Objective = 33.5/2;
H_Objective = 61.6;
h_Objective = 11.5;
r_Objective = 4.7/2;
focus = 1.9;


// // // // // Holder // // // // //

module posHolder(){
    translate([x_HolderPos,y_HolderPos,z_HolderPos])cube([x_Holder,y_Holder,z_Holder]);
    translate([pos_x_Holder_Support,y_HolderPos,h_Screen/2-z_Glass-3.49-Walls])cube([15.4,y_Holder,z_HolderPos-(h_Screen/2-z_Glass-3.49-Walls)]);
}

module negHolder(){
    translate([x_ScrewPos,y_HolderPos+y_ScrewPos,z_ScrewPos])cylinder(r=Screw_M6, h=z_Holder, $fn=Smoothness);
    translate([x_ScrewPos,-y_HolderPos-y_ScrewPos,z_ScrewPos])cylinder(r=Screw_M6, h=z_Holder, $fn=Smoothness);
    
}

if (Holder==1){rotate([0,0,$t*tt])translate([0,0,-(h_Screen/2-z_Glass-1+Bottom+z_Glass+tol+8/18.18+7.5)])difference(){
    posHolder();
    negHolder();
    }
}

// // // // // Fish Tank // // // // //

module posTank(){

      translate([0,y_Minkowski,0])
        minkowski(){
            cylinder (r1= r1, r2= r2, h= h_r1_r2, $fn= Smoothness);
            rotate([0,0,180])cube ([x_Tank,y_Tank,z_Tank]);
        }//First Level Positive
        
      translate([0,y_Minkowski,h_r1_r2])
        minkowski(){
            cylinder (r1= r2, r2= r3, h= h_r2_r3, $fn=Smoothness);
            rotate([0,0,180])cube ([x_Tank,y_Tank,z_Tank]);
        }//Second Level Positive 
}

module Water_Saving_outside(){
    rotate(rotation)translate([-158-11,-200,Bottom-7.5])cube([100,200,24]);
    rotate(rotation)translate([-x_Glass/2-Walls-100,-y_Glass/2-Walls-y_Minkowski-100,Bottom-7.5])cube([105,101.6,24]);
}
module Water_Saving_inside(){
    rotate(rotation)translate([-158-12,-200,Bottom-7.5])cube([100,200,36.5]);
    rotate(rotation)translate([-x_Glass/2-Walls-100,-y_Glass/2-Walls-y_Minkowski-100,Bottom-7.5])cube([105,101.6+5,36.5]);
    rotate(rotation)translate([-x_Glass/2-Walls-100-28,-y_Glass/2-Walls-y_Minkowski-100,Bottom-7.5])cube([105,101.6+14,36.5]);
}
        
module negTank() { 

    difference(){
        translate([0,y_Minkowski,Walls])
            difference(){
                minkowski(){
                    cylinder (r1= r1-Walls, r2= r2-Walls, h= h_r1_r2-Walls, $fn= Smoothness);
                    rotate([0,0,180])cube ([x_Tank,y_Tank,z_Tank]);
                }
                Water_Saving_inside();
            }//First Level Negative
            
        translate([pos_x_Holder_Support,-250,0])cube([Walls,500,h_Tank+Walls]);//First Level Left Wall
        rotate(rotation)translate([x_HolderPos-250,-x_HolderPos-x_Holder+Walls+Margin,0])cube([500,Walls,h_Tank+Walls]);//First Level Back Wall 
            
        difference(){
            union(){
                rotate([0,0,rotation])translate([SealHole+Walls,SealHole+Walls,0])cube([Walls,500,h_Tank+Walls]);// First Level Right Rotated Wall
                rotate([0,0,rotation])translate([SealHole+Walls,SealHole+Walls,0])mirror([0,1,0])cube([Walls,500,h_Tank+Walls]);// First Level Right Rotated Wall
            }
             union(){
        translate([cos(rotation)*(SealHole),sin(rotation)*(SealHole),Bottom])rotate([0,0,rotation])cube([3*Walls,(Format*h_Screen)/2,h_Screen]);//Screen
        translate([cos(rotation)*(SealHole),sin(rotation)*(SealHole),Bottom])rotate([0,0,rotation])mirror([0,1,0])cube([3*Walls,(Format*h_Screen)/2,h_Screen]);//Screen
             }
        }
        translate([x_HolderPos-250,-250,0])cube([500,500,Bottom]);//Bottom
}
     
      difference(){
        translate([0,y_Minkowski,h_r1_r2])
        difference(){
            minkowski(){
                cylinder (r1= r2-Walls, r2= r3-Walls, h= h_r2_r3, $fn=Smoothness);
                rotate([0,0,180])cube ([x_Tank,y_Tank,z_Tank]);
            }
            translate([0,0,Walls-h_r1_r2])Water_Saving_inside();
        }//Second Level Negative

        translate([pos_x_Holder_Support,-250,0])cube([Walls,500,h_Tank+Walls]);//Second Level Left Wall
        rotate(rotation)translate([x_HolderPos-250,-x_HolderPos-x_Holder+Walls+Margin,h_r1_r2])cube([500,Walls,h_Tank+Walls]);//Second Level Back Wall 

         difference(){
             union(){
                 rotate([0,0,rotation])translate([SealHole+Walls,SealHole+Walls,h_r1_r2])cube([Walls,500,h_Tank+Walls]);// Second Level Right Rotated Wall
                 rotate([0,0,rotation])translate([SealHole+Walls,SealHole+Walls,h_r1_r2])mirror([0,1,0])cube([Walls,500,h_Tank+Walls]);// Second Level Right Rotated Wall  
             }
             union(){
        translate([cos(rotation)*(SealHole),sin(rotation)*(SealHole),Bottom])rotate([0,0,rotation])cube([3*Walls,(Format*h_Screen)/2,h_Screen]);//Screen
        translate([cos(rotation)*(SealHole),sin(rotation)*(SealHole),Bottom])rotate([0,0,rotation])mirror([0,1,0])cube([3*Walls,(Format*h_Screen)/2,h_Screen]);//Screen
             }
         }     
}

rotate(rotation){
    translate([-x_Glass/2+Walls,-y_Glass/2+Walls,0])cube([x_Glass-2*Walls,y_Glass-2*Walls,Bottom]);
translate([-x_Glass/2-tol,-y_Glass/2-tol,0])cube([x_Glass+2*tol,y_Glass+2*tol,z_Glass+tol]); // Bottom Glass  
}
 
translate([pos_x_Holder_Support-100,-250,0])cube([100,500,100]);//Left Wall Negative
rotate(rotation)translate([x_HolderPos-250,-x_HolderPos-x_Holder+2*Walls+Margin,0])cube([500,250,h_Tank+Walls]);//Back Wall Negative
    
rotate([0,0,rotation])translate([SealHole+2*Walls,SealHole+2*Walls,0])cube([250,500,h_Tank+Walls]);//Right Wall Negative
rotate([0,0,rotation])translate([SealHole+2*Walls,SealHole+2*Walls,0])mirror([0,1,0])cube([250,500,h_Tank+Walls]);//Right Wall Negative 

translate([-Walls,y_Minkowski-Walls,-Walls])Water_Saving_outside();
}
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

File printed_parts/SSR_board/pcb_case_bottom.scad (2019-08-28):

boardx=98;
boardy=78;
boardz=1.6;
$fn=20;



module pcbpin(){
cylinder(d=6,h=12,center=true);
    translate([0,0,7]){
cylinder(d=2.9,h=2,center=true);
    }//translate
}//module



module board(){
    difference(){
cube([boardx,boardy,boardz],center=true);
union(){
translate([boardx/2-6,boardy/2-6,0]){
cylinder(d=3.1,h=2,center=true);  
}//translate

translate([-boardx/2+6,boardy/2-6,0]){
cylinder(d=3.1,h=2,center=true);  
}//translate

translate([-boardx/2+6,-boardy/2+6,0]){
cylinder(d=3.1,h=2,center=true);  
}//translate

translate([boardx/2-6,-boardy/2+6,0]){
cylinder(d=3.1,h=2,center=true);  
}//translate
}//union
}//difference
}//module

module box(){
    difference(){
    cube([boardx+8,boardy+8,12],center=true);
    translate([0,0,1]){
    cube([boardx+2,boardy+2,12],center=true);
    }//translate
}//difference





    }//module


%board();
translate([boardx/2-6,-boardy/2+6,6]){
pcbpin();
    }//translate

translate([-boardx/2+6,-boardy/2+6,6]){
pcbpin();
    }//translate
    
translate([boardx/2-6,boardy/2-6,6]){
pcbpin();
    }//translate
    
translate([-boardx/2+6,boardy/2-6,6]){
pcbpin();
    }//translate
translate([0,0,6]){
box();
}
//}

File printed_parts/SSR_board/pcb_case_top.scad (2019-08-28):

boardx=98;
boardy=78;
boardz=1.6;
$fn=20;

//distance of the screw hole to the closest edge of the board
bhdis=6;

box_space=8;

bncx=15;
bncy=bncx;
bncz=22;

potx=5;
poty=5;
potz=22;
module pcbpin(){
cylinder(d=6,h=12,center=true);
    translate([0,0,7]){
cylinder(d=2.9,h=2,center=true);
    }//translate
}//module

module bnch(){
   cube([bncx,bncy,bncz],center=true); 
    }

module poth(){
    cube([potx,poty,potz],center=true);
    }
module board(){
    difference(){
cube([boardx,boardy,boardz],center=true);
union(){
translate([boardx/2-6,boardy/2-6,0]){
cylinder(d=3.1,h=2,center=true);  
}//translate

translate([-boardx/2+6,boardy/2-6,0]){
cylinder(d=3.1,h=2,center=true);  
}//translate

translate([-boardx/2+6,-boardy/2+6,0]){
cylinder(d=3.1,h=2,center=true);  
}//translate

translate([boardx/2-6,-boardy/2+6,0]){
cylinder(d=3.1,h=2,center=true);  
}//translate
}//union
}//difference
}//module

module box(){
    difference(){
    cube([boardx+box_space,boardy+box_space,24],center=true);
    translate([0,0,1]){
    cube([boardx+4,boardy+4,24],center=true);
    }//translate
}//difference





    }//module

/*
%board();
translate([boardx/2-bhdis,-boardy/2+bhdis,6]){
pcbpin();
    }//translate

translate([-boardx/2+bhdis,-boardy/2+bhdis,6]){
pcbpin();
    }//translate
    
translate([boardx/2-bhdis,boardy/2-bhdis,6]){
pcbpin();
    }//translate
    
translate([-boardx/2+bhdis,boardy/2-bhdis,6]){
pcbpin();
    }//translate
*/
difference(){
translate([0,0,12]){
box();
}//translate

union(){
////////SIDE1///////////////////////////////////////////////////
translate([(boardx)/2-(bhdis+(bncx/2)+12),-(boardy/2+4),14]){
bnch();
}//translate

translate([(boardx)/2-(bhdis+(bncx/2)+12+bncx+2),-(boardy/2+4),14]){
bnch();
}//translate

translate([(boardx)/2-(bhdis+(bncx/2)+12+2*bncx+4),-(boardy/2+4),14]){
bnch();
}//translate

translate([(boardx)/2-(bhdis+(bncx/2)+12+3*bncx+6),-(boardy/2+4),14]){
bnch();
}//translate
//////////////////////////////////////////////////////////////

/////SIDE2//////////////////////////////////////////////////////////
translate([(boardx)/2-(bhdis+(bncx/2)+12),(boardy/2+4),14]){
bnch();
}//translate

translate([(boardx)/2-(bhdis+(bncx/2)+12+bncx+2),(boardy/2+4),14]){
bnch();
}//translate

translate([(boardx)/2-(bhdis+(bncx/2)+12+2*bncx+4),(boardy/2+4),14]){
bnch();
}//translate

translate([(boardx)/2-(bhdis+(bncx/2)+12+3*bncx+6),(boardy/2+4),14]){
bnch();
}//translate

/////////////////////////////////////////////////////////////////

///////blanking///////////////////////////////////////
translate([-(boardx/2+1),(boardy)/2-(bhdis+(bncy/2)+9),14]){
bnch();
}//translate
///////////////////////////////////////////////////
translate([boardx/2+2.5,-(boardy)/2+(bhdis+11.5),14]){
poth();
}//translate

translate([boardx/2+2.5,-(boardy)/2+(bhdis+29.5),14]){
poth();
}//translate

translate([-(boardx/2+2.5),-(boardy)/2+(bhdis+11.5),14]){
poth();
}//translate

translate([-(boardx/2+2.5),-(boardy)/2+(bhdis+29.5),14]){
poth();
}//translate
translate([-(bncy+2),-boardy/2+2,-0.5]){
rotate([0,0,180])
mirror(){
linear_extrude(1.3){
text("LCrG",size=3.5);
}//mirror
    }//linear_extrude
}//translate


translate([-(2*bncy+4),-boardy/2+2,-0.5]){
rotate([0,0,180])
mirror(){
linear_extrude(1.3){
text("LEDG",size=3.5);
}//mirror
    }//linear_extrude
}//translate

translate([-(bncy+2),boardy/2,-0.5]){
rotate([0,0,180])
mirror(){
linear_extrude(1.3){
text("LCrUV",size=3.5);
}//mirror
    }//linear_extrude
}//translate

translate([-(2*bncy+4),boardy/2,-0.5]){
rotate([0,0,180])
mirror(){
linear_extrude(1.3){
text("LEDUV",size=3.5);
}//mirror
    }//linear_extrude
}//translate

}//union
}


//translate([-(boardx/2+1),(boardy)/2-(bhdis+(bncy/2)+9),14]){
//rotate([0,90,0]){
//cylinder(d=12,h=10,center=true);
  //  }
//}

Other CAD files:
printed_parts/optical_components/lcr_addons/light guide holder.3mf
printed_parts/optical_components/lcr_addons/LCr_tilter/Lcr_tilter.stl
printed_parts/optical_components/ND_filter_holder/ND_filterholder_large_filter.3mf
printed_parts/optical_components/fish_stimulator/dichroic_holder.stl
printed_parts/optical_components/fish_stimulator/DMD_lens_adapter.scad
printed_parts/optical_components/ND_filter_holder/ND_filter_socks.3mf
printed_parts/optical_components/ND_filter_holder/ND_filterholder.3mf
printed_parts/optical_components/ND_filter_holder/ND_filterholder.scad
printed_parts/optical_components/ND_filter_holder/ND_filterholder_rigid_plastic.scad
printed_parts/optical_components/ND_filter_holder/filter_hanger.3mf
printed_parts/optical_components/fish_stimulator/Optical Components.scad
printed_parts/optical_components/lcr_addons/LCr_tilter/Lcr_tilter.scad
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

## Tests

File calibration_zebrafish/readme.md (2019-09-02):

## Calibration scripts (fish)

`stimulator_calibration.ipynb` - This iPython notebook allows estimating photoceptor excitation caused by a combination of light sources (e.g. LEDs) and dichroic filters used in a visual stimulator. To this end, spectral data is recorded with Thorlabs spectometer (model CCS200/M) and the power of each LED is measured with a thorlabs powermeter (PM100D) and accompanying sensor (S130VC). These data are combined and converted into photoisomerization rates per cone photoreceptor type and LED.

It demonstrates the calibration of a tetrachromatic stimulator with red, blue, green and UV LEDs for Zebrafish larvae, but it can be easily adapted to other light sources, as well as more and different spectral opsin sensitivities. For more details, see documentation in the notebook.

`opsin_spectra.ipynb` - This iPython notebook calculates opsin absorbance spectra as described in [Govardovskii *et al.* (2000)](https://www.cambridge.org/core/journals/visual-neuroscience/article/in-search-of-the-visual-pigment-template/A4738E821720092B7F5A233C4AB4962B).

`silent_substitution_protocol.ipynb` - This iPython notebook proposes a silent substitution protocol by spectral compensation for generating opsin-isolating stimuli that account for the cross-activation of zebrafish opsins by the LEDs.

Here, one opsin type is selectively stimulated by presenting a scaled, counterphase version of the stimulus to all other opsin types.

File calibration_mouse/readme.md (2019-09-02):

## Calibration scripts (mouse)

`stimulator_calibration.ipynb` - This iPython notebook allows estimating photoceptor excitation caused by a combination of light sources (e.g. LEDs) and dichroic filters used in a visual stimulator. To this end, spectral data from an Ocean Optics spectometer is recorded via USB (i.e. with the USB2000+ spectrometer, Ocean Optics) and converted into photoisomerization rates per cone photoreceptor type and LED. 

It demonstrates the calibration of a dichromatic stimulator with green/UV LEDs for mice, but it can be easily adapted to other light sources, as well as more and different spectral opsin sensitivities. For more details, see documentation in the notebook.

`opsin_spectra.ipynb` - This iPython notebook calculates opsin spectra as described in [Stockman and Sharpe (2000)](https://www.sciencedirect.com/science/article/pii/S0042698900000213).

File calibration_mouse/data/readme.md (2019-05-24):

`LEDs_Setup2_20180821` - Measurement of the intensity curve (128 levels, from 0 to 254 in steps of 2) for the UV and the 
green LED to estimate the gamma correction look-up table (LUT, `defaultGammaLUT.txt`). Note that LED power was increased 
compare to the normal experimental conditions (i.e. retina recordings) to yield spectrometer readings in the low level range. 

`LEDs_Setup2_20180823` - Measurement of the intensity curve (128 levels, from 0 to 254 in steps of 2) for the UV and the 
green LED **with gamma-correction** applied. Note that like for `LEDs_Setup2_20180821`, LED power was increased 
compare to the normal experimental conditions to yield spectrometer readings in the low level range. 

`LEDs_Setup2_20190130` - Measurement of maximal intensity (only level 255) of the UV and the green LED **after adjusting 
the LED power** to the range used for retina recordings. 

`TFTMonitor_Samsung_4` - Measurement of a random TFT monitor.

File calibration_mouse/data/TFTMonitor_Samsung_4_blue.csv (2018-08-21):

 | wavelength | raw_bkg | raw_avg0 | raw_avg17 | raw_avg34 | raw_avg51 | raw_avg68 | raw_avg85 | raw_avg102 | raw_avg119 | raw_avg136 | raw_avg153 | raw_avg170 | raw_avg187 | raw_avg204 | raw_avg221 | raw_avg238 | raw_avg255
0 | 338.6034821 | 15.818793103448275 | 0.0 | 0.0 | 0.0 | 0.0 | 0.0 | 0.0 | 0.0 | 0.0 | 0.0 | 0.0 | 0.0 | 0.0 | 0.0 | 0.0 | 0.0 | 0.0
1 | 338.99251968121007 | 25635.484137931035 | 0.0 | 0.0 | 0.0 | 0.0 | 0.0 | 0.0 | 0.0 | 0.0 | 0.0 | 0.0 | 0.0 | 0.0 | 0.0 | 0.0 | 0.0 | 0.0
2 | 339.3815129420806 | 620.322672413793 | 30.50767241379316 | 4.51965517241382 | -3.389741379310294 | -25.988017241379225 | -2.259827586206825 | 5.649568965517346 | 48.58629310344833 | 19.208534482758694 | 14.688879310344873 | -46.32646551724133 | -46.326465517241274 | 37.28715517241386 | 28.247844827586277 | 11.299137931034522 | -10.16922413793094 | 15.818793103448343
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

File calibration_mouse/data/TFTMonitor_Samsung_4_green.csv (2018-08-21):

 | wavelength | raw_bkg | raw_avg0 | raw_avg17 | raw_avg34 | raw_avg51 | raw_avg68 | raw_avg85 | raw_avg102 | raw_avg119 | raw_avg136 | raw_avg153 | raw_avg170 | raw_avg187 | raw_avg204 | raw_avg221 | raw_avg238 | raw_avg255
0 | 338.6034821 | 15.818793103448275 | 0.0 | 0.0 | 0.0 | 0.0 | 0.0 | 0.0 | 0.0 | 0.0 | 0.0 | 0.0 | 0.0 | 0.0 | 0.0 | 0.0 | 0.0 | 0.0
1 | 338.99251968121007 | 25635.484137931035 | 0.0 | 0.0 | 0.0 | 0.0 | 0.0 | 0.0 | 0.0 | 0.0 | 0.0 | 0.0 | 0.0 | 0.0 | 0.0 | 0.0 | 0.0 | 0.0
2 | 339.3815129420806 | 618.0628448275861 | -30.50767241379299 | -12.429051724137821 | -7.909396551724058 | -28.247844827586107 | 10.169224137931167 | 15.818793103448343 | 5.649568965517346 | 21.468362068965632 | 28.247844827586334 | 19.208534482758694 | 31.637586206896685 | 15.8187931034484 | 11.29913793103458 | 6.779482758620816 | -16.94870689655164 | -46.326465517241274
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

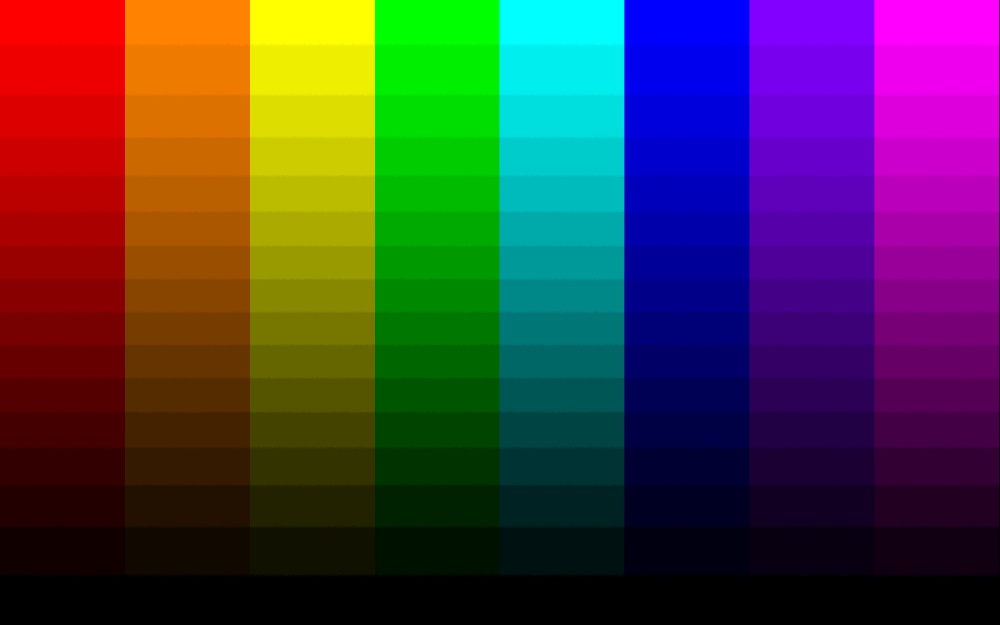
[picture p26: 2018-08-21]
calibration_mouse_invivo/datasheets/color_bar_test_image.jpg

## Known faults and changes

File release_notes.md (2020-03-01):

## Release notes

#### 2020-02-11
- We noticed that [EKB](https://www.ekbtechnologies.com/) recently changed their part numbers and that the part numbers are confusing. Therefore, some of the LCr related information given in [Table 2](https://elifesciences.org/articles/48779#table2) in Franke at al. (2019) is incorrect. Here is the (currently) correct ordering information:

    - Follow this [link](https://www.ekbtechnologies.com/e-store/dlp-lightcrafter-e4500-mkii-fiber-couple?c=5cb86ca038d9a) to        find the 0.45' ‘DLP Fiber couple E4500MKII Development Module.  
    - **Important: For the solution we decribe in the paper, make sure that you selected the fiber type "LLG" (for Thorlab's light guide).**  
    - Note that the part number still seems `DPM-E4500MKIIFC` - which is a bit confusing. Therefore make sure that EKB knows what fibre adapter you need.

#### 2019-10-04
- Added a new folder ([`/printed_parts/optical_components/lcr_addons`](https://github.com/eulerlab/open-visual-stimulator/tree/master/printed_parts/optical_components/lcr_addons)) for additional parts provided by users.
- New mechanical part to couple a light guide into an LED port of a "standard" lighcrafter (`fibre_coupler`). Contributed by David Ide, Biomedical Engineering Technician, NIMH Section on Instrumentation.

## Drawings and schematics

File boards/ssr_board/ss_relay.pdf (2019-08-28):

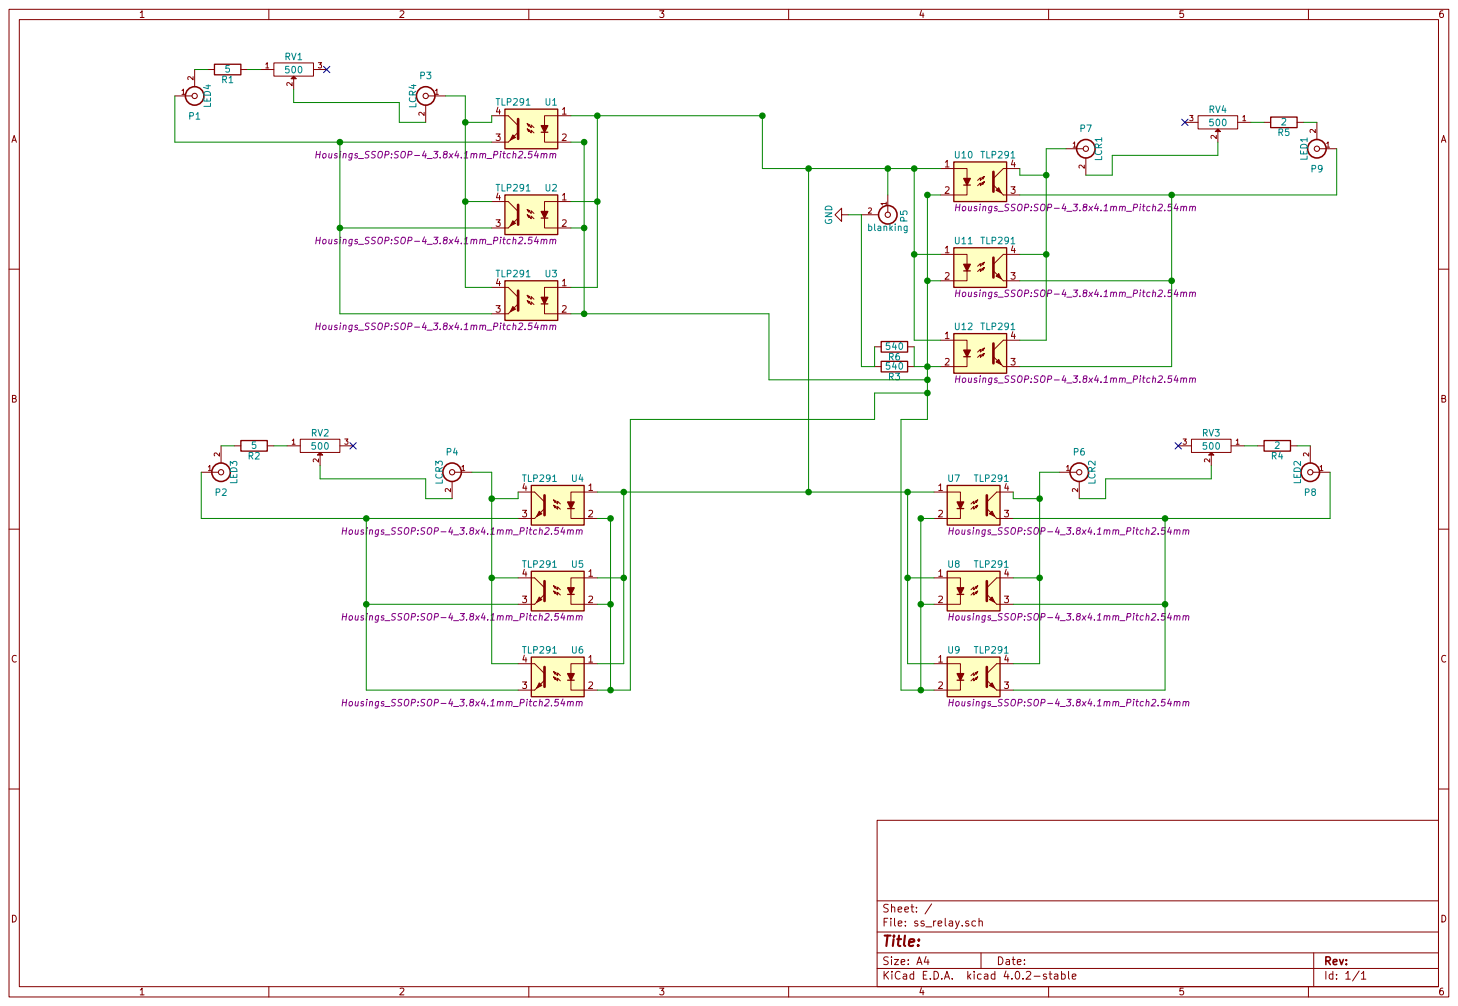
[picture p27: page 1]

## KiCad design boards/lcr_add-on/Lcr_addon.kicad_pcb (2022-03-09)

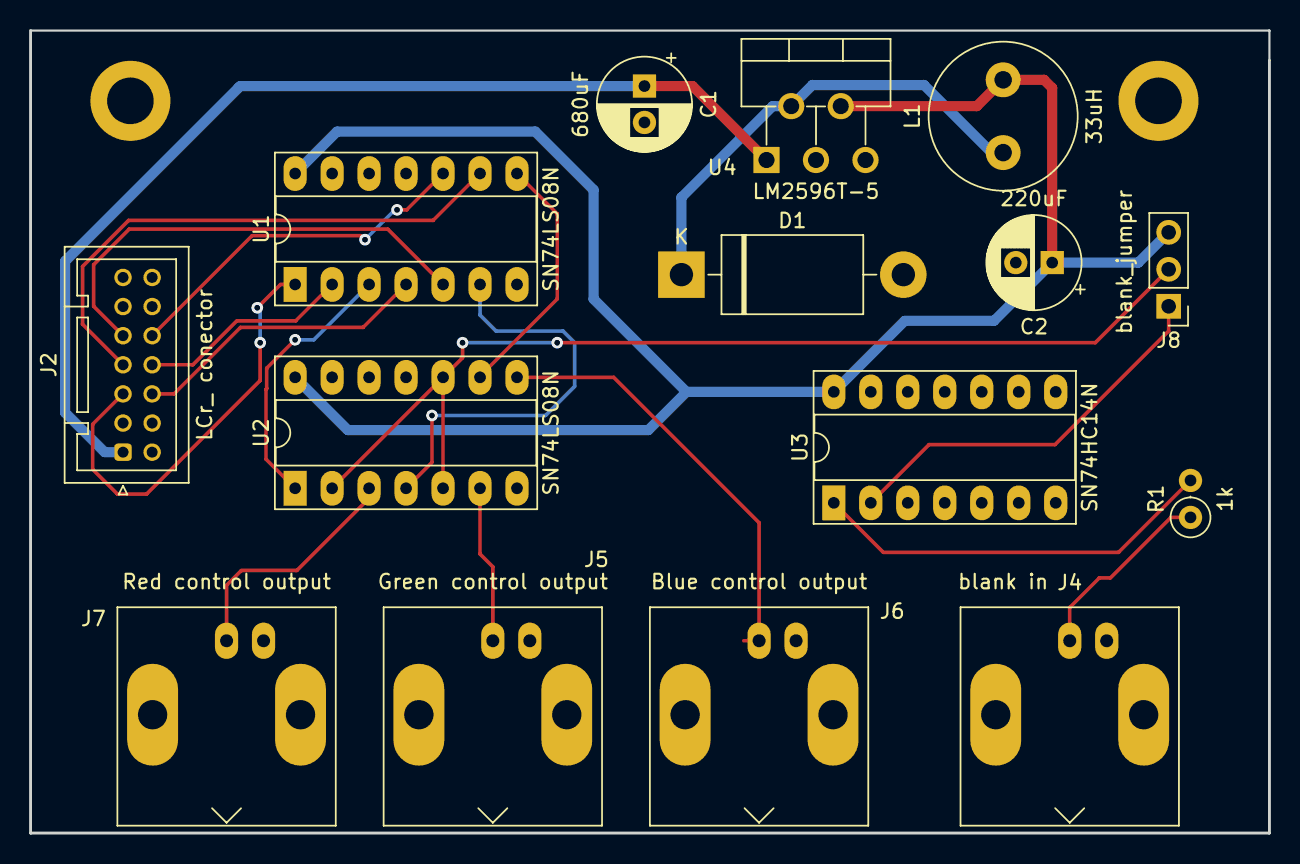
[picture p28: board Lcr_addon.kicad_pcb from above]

Board: 2 copper layers, 85.1 x 55.1 mm, 15 parts (0 on the bottom side), 20 nets.

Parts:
C1: 680uF; CP_Radial_D6.3mm_P2.50mm
C2: 220uF; CP_Radial_D6.3mm_P2.50mm
D1: D_Schottky; D_DO-201AD_P15.24mm_Horizontal
J2: LCr_ conector; JST_PUD_B14B-PUDSS_2x07_P2.00mm_Vertical
J4: blank in; BNC_Amphenol_B6252HB-NPP3G-50_Horizontal
J5: Green control output; BNC_Amphenol_B6252HB-NPP3G-50_Horizontal
J6: Blue control output; BNC_Amphenol_B6252HB-NPP3G-50_Horizontal
J7: Red control output; BNC_Amphenol_B6252HB-NPP3G-50_Horizontal
J8: blank_jumper; PinHeader_1x03_P2.54mm_Vertical
L1: 33uH; L_Radial_D10.0mm_P5.00mm_Neosid_SD12_style3
R1: 1k; R_Axial_DIN0207_L6.3mm_D2.5mm_P2.54mm_Vertical
U1, U2: SN74LS08N; DIP-14_W7.62mm_Socket_LongPads
U3: SN74HC14N; DIP-14_W7.62mm_Socket_LongPads
U4: LM2596T-5; TO-220-5_P3.4x3.7mm_StaggerOdd_Lead3.8mm_Vertical

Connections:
+5V: C2.1, J8.3, L1.2, U1.14, U2.14, U3.14, U4.4
+12V: C1.1, J2.1, U4.1
GND: C1.2, C2.2, D1.2, J2.12, J2.13, J2.14, J4.2, J5.2, J6.2, J7.2, U1.7, U2.7, U3.7, U4.3, U4.5
unnamed: D1.1, L1.1, U4.2
unnamed: J4.1, R1.1
unnamed: J5.1, U2.6
unnamed: J6.1, U2.8
unnamed: J7.1, U2.3
unnamed: R1.2, U3.1
unnamed: U1.3, U2.1
unnamed: U1.6, U2.4
unnamed: U1.8, U2.9
blue_sig1: J2.7, U1.9
blue_sig2: J2.10, U1.10
green_sig1: J2.6, U1.4
green_sig2: J2.9, U1.5
inv_blank-or-5V-input: J8.2, U2.2, U2.5, U2.10
inverted_blank: J8.1, U3.2
red_sig1: J2.5, U1.1
red_sig2: J2.8, U1.2

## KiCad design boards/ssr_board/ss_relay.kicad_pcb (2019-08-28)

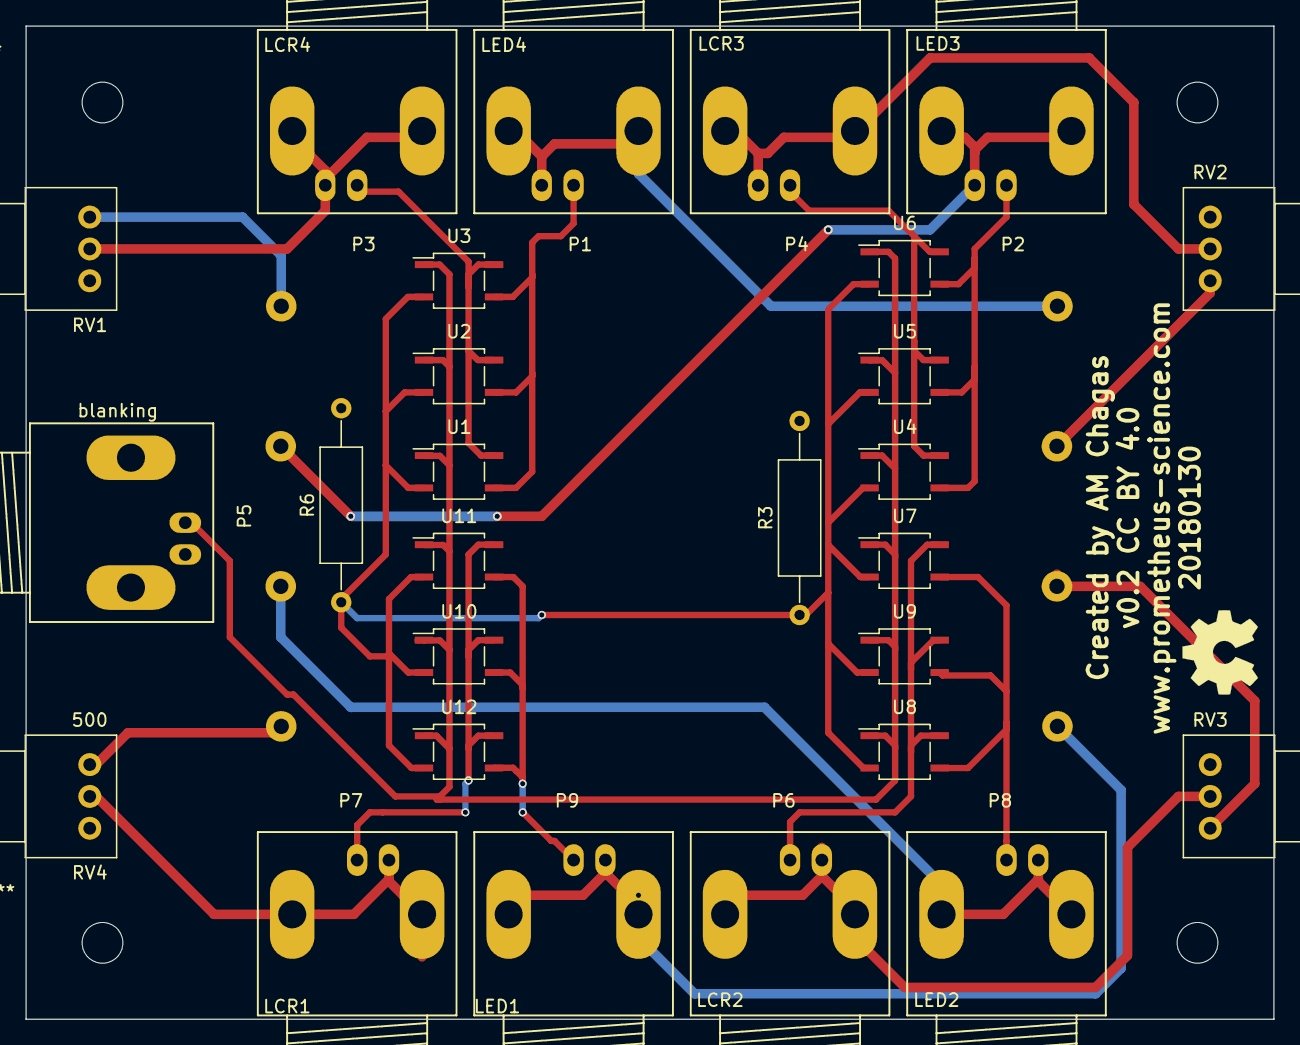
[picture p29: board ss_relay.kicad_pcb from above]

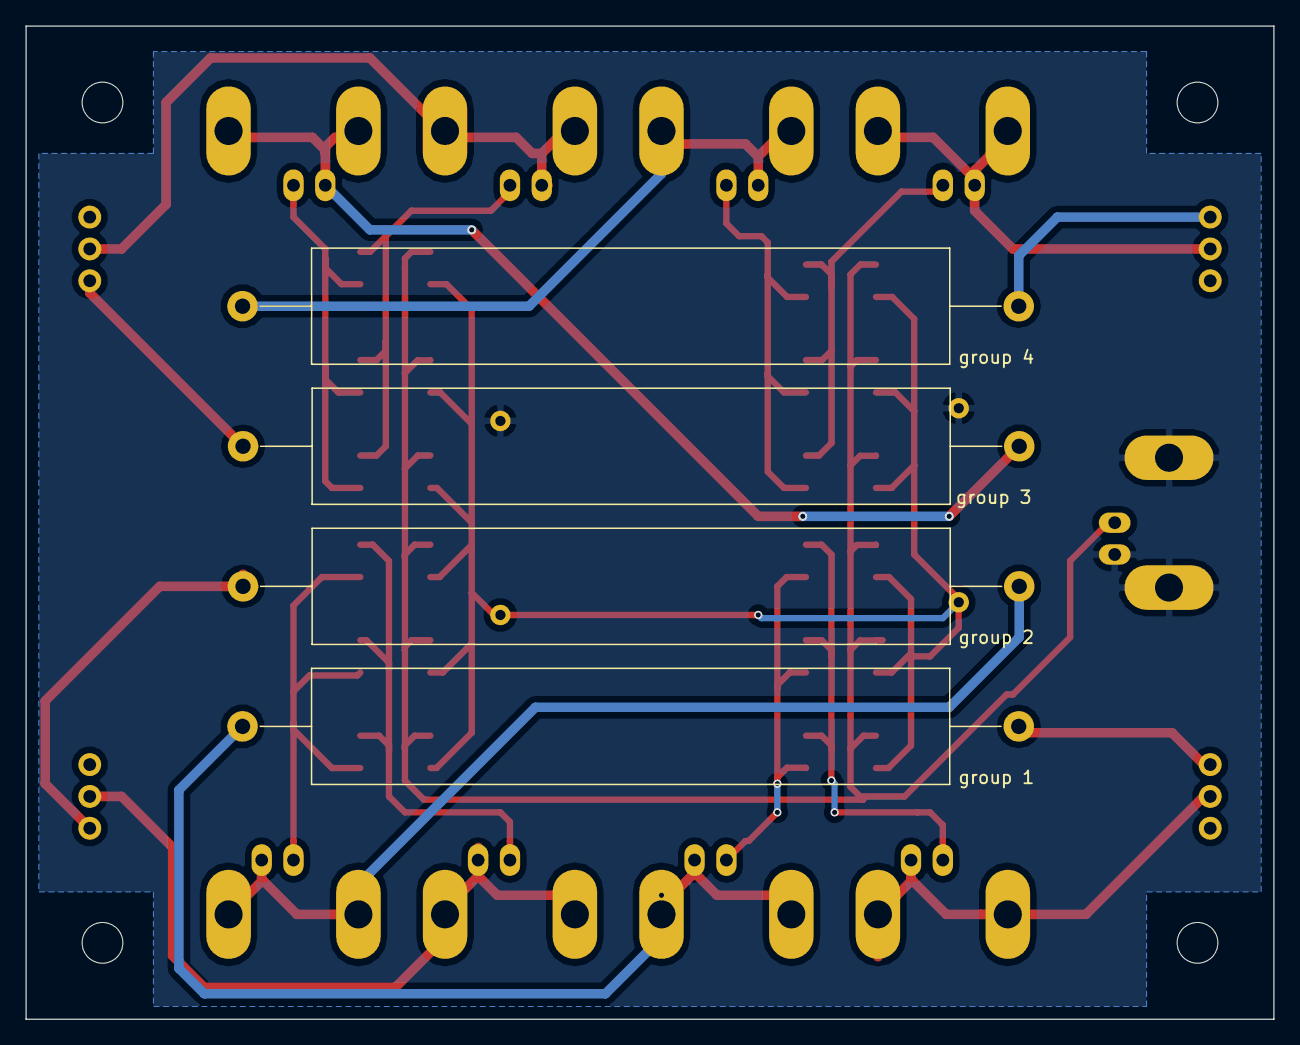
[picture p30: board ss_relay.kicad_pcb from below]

Board: 2 copper layers, 98.0 x 78.0 mm, 31 parts (4 on the bottom side), 23 nets.

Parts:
P1: LED4; BNC_Socket_TYCO-AMP_LargePads
P2: LED3; BNC_Socket_TYCO-AMP_LargePads
P3: LCR4; BNC_Socket_TYCO-AMP_LargePads
P4: LCR3; BNC_Socket_TYCO-AMP_LargePads
P5: blanking; BNC_Socket_TYCO-AMP_LargePads
P6: LCR2; BNC_Socket_TYCO-AMP_LargePads
P7: LCR1; BNC_Socket_TYCO-AMP_LargePads
P8: LED2; BNC_Socket_TYCO-AMP_LargePads
P9: LED1; BNC_Socket_TYCO-AMP_LargePads
R3, R6: 270; R_Axial_DIN0309_L9.0mm_D3.2mm_P15.24mm_Horizontal
RV1, RV2, RV3, RV4: 500; Potentiometer_Alps_RK097_Single_Vertical
U1, U2, U3, U4, U5, U6, U7, U8, U9, U10, U11, U12: TLP291; SOP-4_3.8x4.1mm_Pitch2.54mm
group 1, group 2, group 3, group 4: 10; R_Axial_Power_L50.0mm_W9.0mm_P60.96mm

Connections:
GND: P5.2, R3.2, R6.2
unnamed: P1.1, U1.3, U2.3, U3.3
unnamed: P1.2, group 4.1
unnamed: P2.1, U4.3, U5.3, U6.3
unnamed: P2.2, group 3.1
unnamed: P3.1, U1.4, U2.4, U3.4
unnamed: P3.2, RV1.2
unnamed: P4.1, U4.4, U5.4, U6.4
unnamed: P4.2, RV2.2
unnamed: P5.1, U1.1, U2.1, U3.1, U4.1, U5.1, U6.1, U7.1, U8.1, U9.1, U10.1, U11.1, U12.1
unnamed: P6.1, U7.4, U8.4, U9.4
unnamed: P6.2, RV3.2
unnamed: P7.1, U10.4, U11.4, U12.4
unnamed: P7.2, RV4.2
unnamed: P8.1, U7.3, U8.3, U9.3
unnamed: P8.2, group 2.1
unnamed: P9.1, U10.3, U11.3, U12.3
unnamed: P9.2, group 1.1
unnamed: RV1.1, group 4.2
unnamed: RV2.1, group 3.2
unnamed: R3.1, R6.1, U1.2, U2.2, U3.2, U4.2, U5.2, U6.2, U7.2, U8.2, U9.2, U10.2, U11.2, U12.2
unnamed: RV3.1, group 2.2
unnamed: RV4.1, group 1.2

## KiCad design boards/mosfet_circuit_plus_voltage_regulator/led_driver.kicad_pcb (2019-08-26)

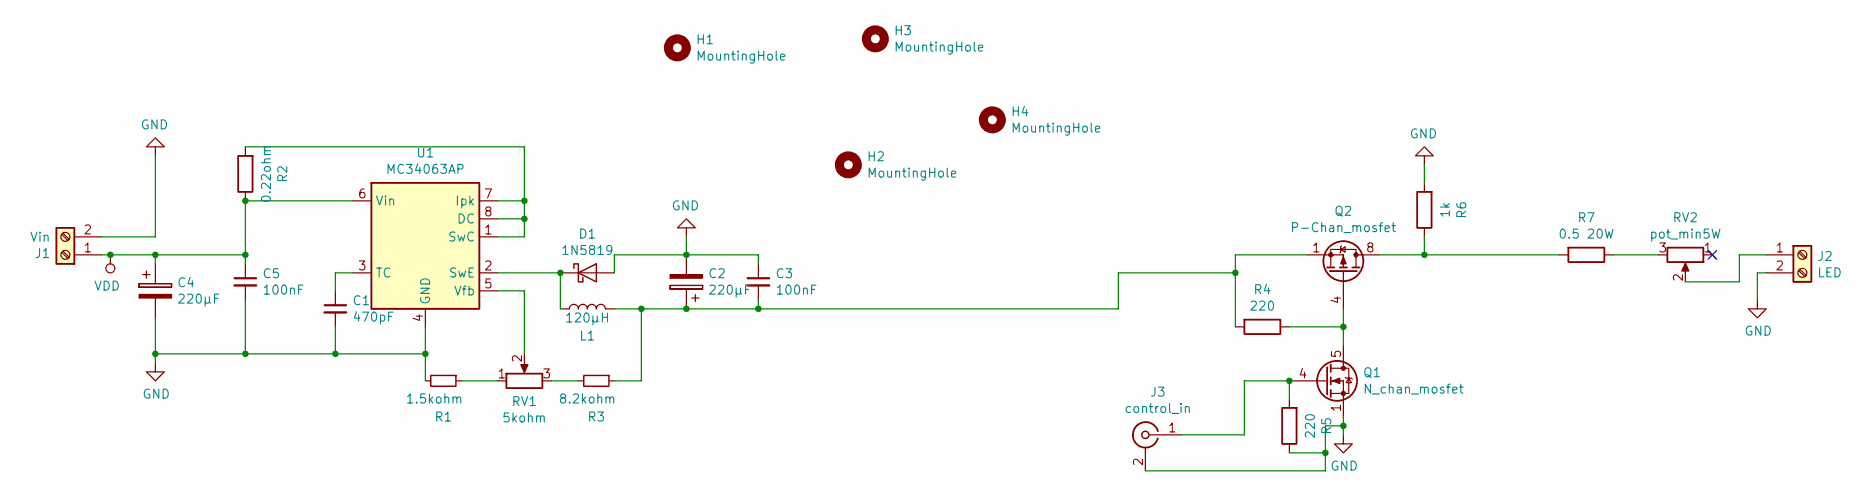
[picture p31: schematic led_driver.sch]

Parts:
C1: 470pF; CP_Radial_D5.0mm_P2.50mm
C2, C4: 220µF; CP_Radial_D8.0mm_P5.00mm
C3, C5: 100nF; C_Disc_D8.0mm_W5.0mm_P7.50mm
D1: 1N5819; D_DO-41_SOD81_P10.16mm_Horizontal
H1, H2, H3, H4: MountingHole; MountingHole_3.2mm_M3
J1: Vin; TerminalBlock_Altech_AK300-2_P5.00mm
J2: LED; TerminalBlock_Altech_AK300-2_P5.00mm
J3: control_in; BNC_Amphenol_B6252HB-NPP3G-50_Horizontal
L1: 120µH; L_Radial_D7.5mm_P5.00mm_Fastron_07P
Q1: N_chan_mosfet; TDSON-8-1
Q2: P-Chan_mosfet; SOIC-8_3.9x4.9mm_P1.27mm
R1: 1.5kohm; R_Axial_DIN0207_L6.3mm_D2.5mm_P10.16mm_Horizontal
R2: 0.22ohm; R_Axial_DIN0414_L11.9mm_D4.5mm_P15.24mm_Horizontal
R3: 8.2kohm; R_Axial_DIN0207_L6.3mm_D2.5mm_P10.16mm_Horizontal
R4, R5: 220; R_Axial_DIN0207_L6.3mm_D2.5mm_P10.16mm_Horizontal
R6: 1k; R_Axial_DIN0207_L6.3mm_D2.5mm_P10.16mm_Horizontal
R7: 0.5 20W; TO-220-2_Vertical
RV1: 5kohm; Potentiometer_Vishay_T73YP_Vertical
RV2: pot_min5W; Potentiometer_ACP_CA14-H5_Horizontal
U1: MC34063AP; DIP-8_W7.62mm

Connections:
GND: C1.2, C2.2, C3.1, C4.2, C5.2, D1.2 (A), J1.2, J2.2, J3.2 (Ext), Q1.1 (S), Q1.2 (S), Q1.3 (S), R1.2, R5.1, R6.2, U1.4 (GND)
unnamed: C1.1, U1.3 (TC)
unnamed: C2.1, C3.2, L1.2, Q2.1 (S), Q2.2 (S), Q2.3 (S), R3.1, R4.2
unnamed: D1.1 (K), L1.1, U1.2 (SwE)
unnamed: J2.1, RV2.2
unnamed: J3.1 (In), Q1.4 (G), R5.2
unnamed: Q1.5 (D), Q2.4 (G), R4.1
unnamed: Q2.5 (D), Q2.6 (D), Q2.7 (D), Q2.8 (D), R6.1, R7.2
unnamed: R1.1, RV1.1
unnamed: R2.2, U1.1 (SwC), U1.7 (Ipk), U1.8 (DC)
unnamed: R3.2, RV1.3
unnamed: R7.1, RV2.3
unnamed: RV1.2, U1.5 (Vfb)
VDD: C4.1, C5.1, J1.1, R2.1, U1.6 (Vin)

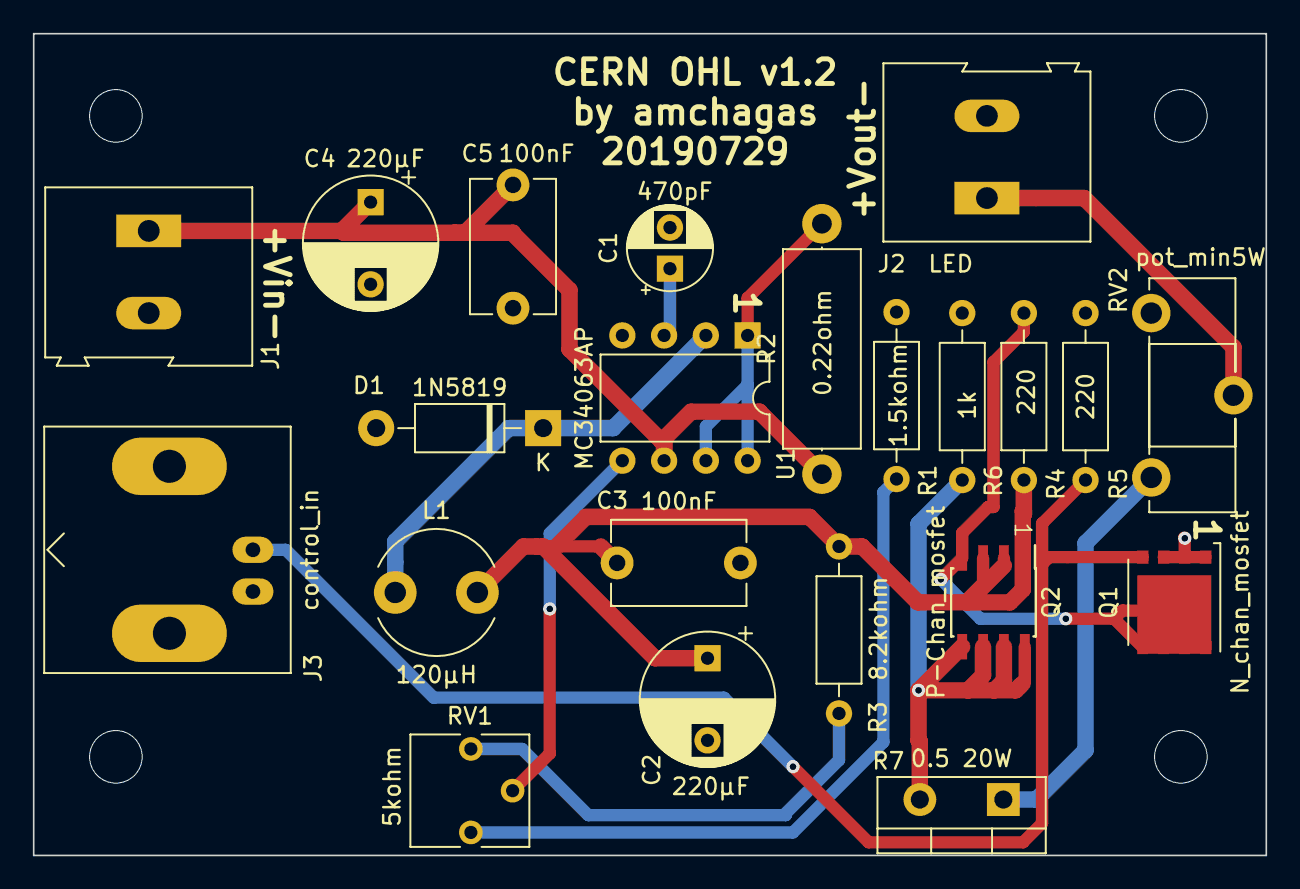
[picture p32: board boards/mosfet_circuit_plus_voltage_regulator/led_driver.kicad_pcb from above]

Board: 2 copper layers, 75.0 x 50.0 mm, 26 parts (0 on the bottom side), 14 nets.

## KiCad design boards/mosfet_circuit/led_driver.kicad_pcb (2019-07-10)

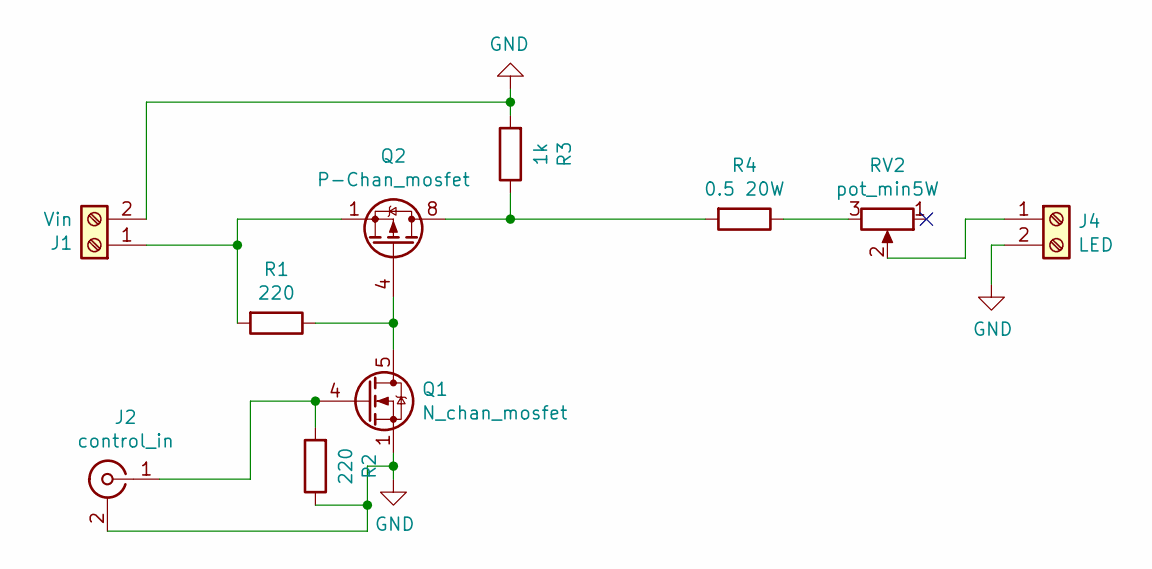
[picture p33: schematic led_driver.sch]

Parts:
J1: Vin; TerminalBlock_Altech_AK300-2_P5.00mm
J2: control_in; BNC_Amphenol_B6252HB-NPP3G-50_Horizontal
J4: LED; TerminalBlock_Altech_AK300-2_P5.00mm
Q1: N_chan_mosfet; TDSON-8-1
Q2: P-Chan_mosfet; SOIC-8_3.9x4.9mm_P1.27mm
R1, R2: 220; R_Axial_DIN0207_L6.3mm_D2.5mm_P10.16mm_Horizontal
R3: 1k; R_Axial_DIN0207_L6.3mm_D2.5mm_P10.16mm_Horizontal
R4: 0.5 20W; R_Axial_DIN0207_L6.3mm_D2.5mm_P10.16mm_Horizontal
RV2: pot_min5W; Potentiometer_ACP_CA14-H5_Horizontal

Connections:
GND: J1.2, J2.2 (Ext), J4.2, Q1.1 (S), Q1.2 (S), Q1.3 (S), R2.1, R3.2
unnamed: J1.1, Q2.1 (S), Q2.2 (S), Q2.3 (S), R1.2
unnamed: J2.1 (In), Q1.4 (G), R2.2
unnamed: J4.1, RV2.2
unnamed: Q1.5 (D), Q2.4 (G), R1.1
unnamed: Q2.5 (D), Q2.6 (D), Q2.7 (D), Q2.8 (D), R3.1, R4.2
unnamed: R4.1, RV2.3

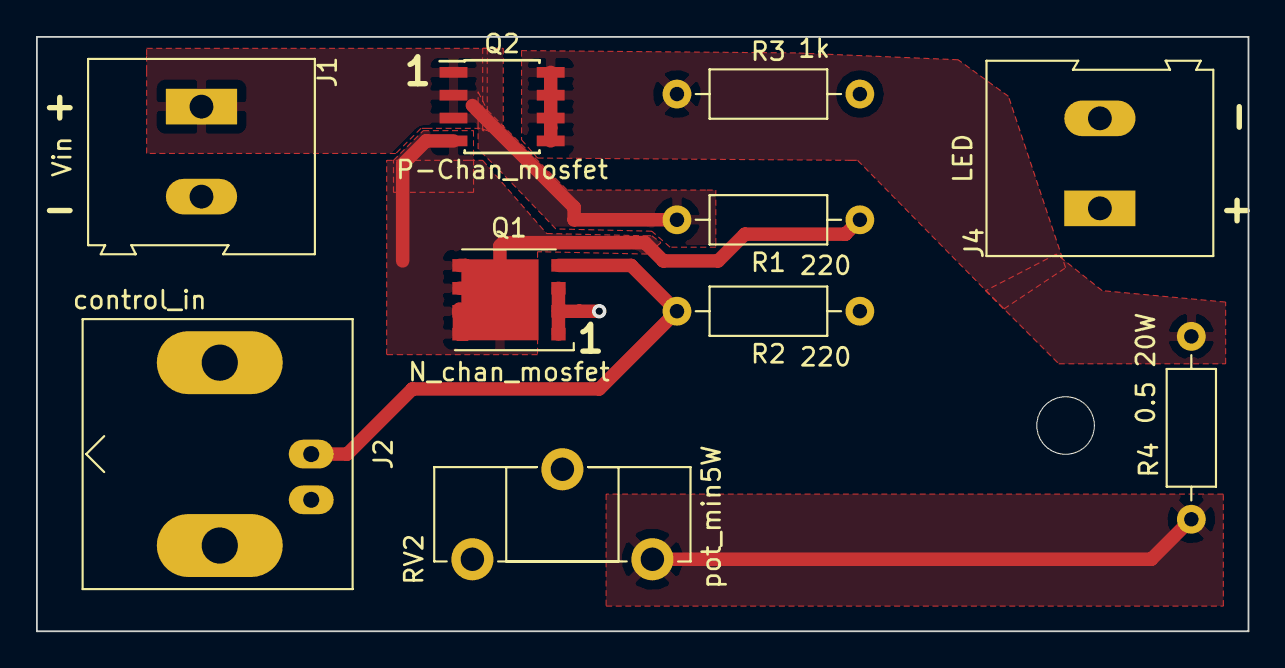
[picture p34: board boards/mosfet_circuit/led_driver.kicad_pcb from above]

Board: 2 copper layers, 67.3 x 33.0 mm, 10 parts (0 on the bottom side), 7 nets.

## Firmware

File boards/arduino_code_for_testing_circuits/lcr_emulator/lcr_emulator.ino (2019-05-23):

// constants won't change. Used here to set a pin number:
const int pin12 =  12;// the number of the LED pin
const int pin11 =  11;// the number of the LED pin
const int pin10 =  10;// the number of the LED pin



// Generally, you should use "unsigned long" for variables that hold time
// The value will quickly become too large for an int to store
unsigned long millis1 = 0;        // will store last time LED was updated
unsigned long millis2 = 0;
unsigned long millis3 = 0;

unsigned long millis12 = 0;        // will store last time LED was updated
unsigned long millis11 = 0;        // will store last time LED was updated
unsigned long millis10 = 0;        // will store last time LED was updated



void setup() {
  // set the digital pin as output:
  pinMode(pin10, OUTPUT);
  pinMode(pin11, OUTPUT);
  pinMode(pin12, OUTPUT);
  millis1=micros();
  millis10=micros();
  millis2=millis();
  millis11=millis();
  millis3=millis();
  millis12=millis();
}

void loop() {
  
  millis10=micros();
  millis11=millis();
  millis12=millis();
  
  if (millis10 - millis1 <= 400) {
    // save the last time you blinked the LED
    digitalWrite(pin10,LOW);
  }
  if (millis10-millis1>400){
    digitalWrite(pin10,HIGH);
  }
    if (millis10-millis1>=2000){
      millis1=micros();
      
  }

  if (millis11-millis2<=5){
    digitalWrite(pin11,HIGH);
  }
  if (millis11-millis2>5){
    digitalWrite(pin11,LOW);
  }  
    if (millis11-millis2>=10){
    millis2=millis();
   
  }  

  if (millis12-millis3<=50){
    digitalWrite(pin12,HIGH);
  }
  if (millis12-millis3>50){
    digitalWrite(pin12,LOW);
  }  
    if (millis12-millis3>=100){
    millis3=millis();
   
  }  
}
    

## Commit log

2018-08-09 added information about the fish stimulator
    [BOM.csv]
2018-12-04 first steps for fish stimulator calibration
    Opsin profiles, first changes in jupyter notebook
    [BLUE.csv, GREEN.csv, RED.csv, UV.csv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]
2018-12-07 add lcr emulator code for arduino
2018-12-07 add led spec sheets
2018-12-07 new led driver circuit
    [sketch1.kicad_pcb, sketch1.sch]
2018-12-18 update lm3150 design
    [2018-12-10_03-51-32.brd, 2018-12-10_03-52-40.sch, blanking_new.kicad_pcb, blanking_new.sch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]
2018-12-18 completed lm3150 pcb
    [lm3150-B.Adhes.gbr, lm3150-B.CrtYd.gbr, lm3150-B.Cu.gbr, lm3150-B.Fab.gbr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]
2018-12-19 update to calibration stack
    [BLUE.csv, GREEN.csv, RED.csv, UV.csv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]
2019-03-06 board folder cleanup
    [Lcr_addon-B.Adhes.gbr, Lcr_addon-B.CrtYd.gbr, Lcr_addon-B.Cu.gbr, Lcr_addon-B.Fab.gbr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]
2019-03-06 add voltage and current regulator board, based on lm2596
    [lm2596_cc_vc-B.Adhes.gbr, lm2596_cc_vc-B.CrtYd.gbr, lm2596_cc_vc-B.Cu.gbr, lm2596_cc_vc-B.Fab.gbr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]
2019-03-06 remove old lm2596 driver
    [led_driver-B.Adhes.gbr, led_driver-B.CrtYd.gbr, led_driver-B.Cu.gbr, led_driver-B.Fab.gbr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]
2019-03-06 add back the temp mosfet circuit
    [led_driver-B.Adhes.gbr, led_driver-B.CrtYd.gbr, led_driver-B.Cu.gbr, led_driver-B.Fab.gbr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]
2019-03-07 Create Fish Cinema v10.0_40X_Objective.scad
    add modified fish cinema file
    [Fish Cinema v10.0_40X_Objective.scad]
2019-03-07 added the led spectra readings where the fish would be
    [UV.csv, UV1.csv, UV2.csv, blue.csv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]
2019-03-10 update LCr board
    [BOM.csv, Lcr_addon-B.Adhes.gbr, Lcr_addon-B.CrtYd.gbr, Lcr_addon-B.Cu.gbr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]
2019-03-10 clean up add on board
    [1-click-bom.csv, Lcr_addon-B.Adhes.gbr, Lcr_addon-B.CrtYd.gbr, Lcr_addon-B.Cu.gbr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]
2019-03-10 clean up mosfet circuit
    [1-click-bom.csv, Lcr_addon.kicad_pcb, led_driver-B.Adhes.gbr, led_driver-B.CrtYd.gbr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]
2019-03-11 reorganise led spectra files and add a little code to visualise them
    [UV.csv, UV1.csv, UV2.csv, blue.csv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]
2019-05-08 new board: power supply and sync to led in one
    [Lcr_addon_BOM.csv, led_driver-B.Adhes.gbr, led_driver-B.CrtYd.gbr, led_driver-B.Cu.gbr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]
2019-05-09 Updated
    Cleaned up the main folder and data folder. Files that I think we dont need were put into folder "ToDelete". Created Info text file in data folder with details about the example recordings in this fo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
    [20181004_GaraschukLab_000_Behaviour_white.csv, 20181004_GaraschukLab_001_2P_white.csv, LEDs_Setup2_20180815c_UV.csv, LEDs_Setup2_20180815c_green.csv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]
2019-05-09 update calibration stack
2019-05-09 first org
    [20181004_GaraschukLab_000_Behaviour_white.csv, 20181004_GaraschukLab_001_2P_white.csv, LEDs_Setup2_20190130_0_UV.csv, LEDs_Setup2_20190130_0_green.csv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]
2019-05-09 more org
    [1-click-bom.csv, 2018-12-10_03-51-32.brd, 2018-12-10_03-52-40.sch, BLUE.csv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]
2019-05-11 added cage components
    [LCP30 - modified.stl, Optical Components.scad, dichroic_frame.stl, dichroic_holder.stl]
2019-05-14 added silk information to board
    [lm2596_cc_vc.kicad_pcb]
2019-05-15 added revised version of zebrafish calibration notebook and set some files for deletion
2019-05-23 Cleaning up
    [1-click-bom.csv, 2018-12-10_03-51-32.brd, 2018-12-10_03-52-40.sch, 20181004_GaraschukLab_000_Behaviour_white.csv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]
2019-05-23 zebrafish calibration folder and repo clean up
    [2018-12-10_03-51-32.brd, 2018-12-10_03-52-40.sch, BLUE.csv, GREEN.csv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]
2019-05-23 created scripts folder for zebrafish calibration
2019-05-23 zipped spectrometer files
    [Spectrum000000019.csv, Spectrum000000020.csv, Spectrum000000021.csv, Spectrum000000022.csv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]
2019-05-23 Update spectrometer recording
    [Opsins.csv]
2019-05-23 Update powermeter recording
    [Blue.csv, Green.csv, Red.csv, UV.csv]
2019-05-23 Create Opsin-LED Spectra.png
2019-07-10 preparing boards for kitspace
    [led_driver.kicad_pcb]
2019-07-10 started tracing new board
    [1-click-bom.csv, led_driver-B.Adhes.gbr, led_driver-B.CrtYd.gbr, led_driver-B.Cu.gbr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]
2019-07-10 added information on how to order boards
2019-07-10 final first draft of new board. now to order it and test
    [led_driver-B.Adhes.gbr, led_driver-B.CrtYd.gbr, led_driver-B.Cu.gbr, led_driver-B.Fab.gbr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]
2019-07-10 created first draft of BOM
    [1-click-bom.csv, led_driver.csv]
2019-07-11 add board renderings
2019-07-12 update boms
    [1-click-bom.csv]
2019-07-18 new zebrafish calibration folder
    [Blue.csv, Green.csv, Red.csv, UV.csv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]
2019-07-19 fixed board foot prints
    [led_driver-B.Adhes.gbr, led_driver-B.CrtYd.gbr, led_driver-B.Cu.gbr, led_driver-B.Fab.gbr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]
2019-07-19 created 1-click-bom and updated the folder structure
    [1-click-bom.csv, led_driver-B.Adhes.gbr, led_driver-B.CrtYd.gbr, led_driver-B.Cu.gbr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]
2019-07-19 removed zip from older version of board
2019-07-29 little board clean up, adding license and date
    [led_driver-B.Adhes.gbr, led_driver-B.CrtYd.gbr, led_driver-B.Cu.gbr, led_driver-B.Fab.gbr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]
2019-08-27 adding optocoupler board to repository
    [1-click-bom.csv, pcb_case_bottom.scad, pcb_case_bottom.stl, pcb_case_top.scad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]
2019-08-27 add board rendering
2019-08-27 update 1-click bom optocoupler board
    [1-click-bom.csv]
2019-08-27 1-click bom complete
    [1-click-bom.csv]
2019-08-28 update readmes and 1-click-bom.csv for solid state relay board
    [1-click-bom.csv, ss_relay-B.Adhes.gbr, ss_relay-B.CrtYd.gbr, ss_relay-B.Cu.gbr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]
2019-08-28 update readme ssr board
2019-08-28 update kitpsace.yaml to update ssr board
2019-08-30 update the calibration zebrafish stuff with Max new data
2019-08-30 New STL files
    [LED_holder_plate.scad, LED_holder_plate.stl, mirror_holder.scad, mirror_holder.stl]
2019-08-30 organize printed parts folder
    [Fish Cinema v10.0_40X_Objective.scad, Fish Cinema v10.0_40X_Objective.stl, LCP30 - modified.stl, LED_holder_plate.scad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]
2019-08-30 add DMD lens adapter
    [DMD_lens_adapter.scad, DMD_lens_adapter.stl]
2019-10-03 add fibre coupler design
    [light guide holder.IGS, light guide holder.SLDPRT, light guide holder.STL, light guide holder.x_t]
2019-10-03 change readme at base of printed parts folder
2019-10-08 added Ide's contact info and link to the light guide being used (on readme.md in printed parts)
2019-10-23 update the bom.csv file
    [1-click-bom.csv]
2019-12-20 Spectral calibration for mouse in vivo experiments
    Added calibration file for mouse in vivo imaging. Includes wavelength-dependent transmission of mouse eye
    [LEDs_LCr_20191108_0_UV.csv, LEDs_LCr_20191108_0_blue.csv]
2020-03-01 update 1-click-boms
    [1-click-bom.csv]
2020-03-01 update 1 click boms
    [1-click-bom.csv]
2020-03-04 add printed plates to tilt LCr downwards
    [Lcr_tilter.scad, Lcr_tilter.stl]
2020-03-04 split stls
    [Lcr_tilter.scad, Lcr_tilter_plate1.stl, Lcr_tilter_plate2.stl]
2020-03-05 fine tunning tilt plates
    [Lcr_tilter.scad, Lcr_tilter.stl, Lcr_tilter_plate1.stl, Lcr_tilter_plate2.stl]
2020-03-06 more fine tunning ggrrrrsskjs
    [Lcr_tilter.scad, Lcr_tilter.stl, Lcr_tilter_plate1.stl, Lcr_tilter_plate2.stl]
2020-03-10 remove some material to make print faster, add holes for coupling this to mvs005/m from thorlabs
    [Lcr_tilter.scad, Lcr_tilter.stl, Lcr_tilter_plate1.stl, Lcr_tilter_plate2.stl]
2020-03-12 fixed missing qty for 1-click boms
    [1-click-bom.csv]
2020-04-12 add board pictures
2020-10-21 fix side of nut pocket on Lcr tilter design
    [Lcr_tilter.scad, Lcr_tilter_plate1.stl]
2021-02-17 final wiring for lcr board
    [Lcr_addon.kicad_pcb]
2021-02-17 upload gerbers
    [Lcr_addon-B.Cu.gbr, Lcr_addon-B.Fab.gbr, Lcr_addon-B.Mask.gbr, Lcr_addon-B_Adhes.gbr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]
2021-02-17 final update
    [Lcr_addon.kicad_pcb]
2021-03-17 update board labelling
    [Lcr_addon.kicad_pcb]
2021-03-17 update labelling and 1-click-bom
    [1-click-bom.csv, Lcr_addon-B_Adhes.gbr, Lcr_addon-B_CrtYd.gbr, Lcr_addon-B_Cu.gbr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]
2021-08-03 Add updated calibration notebook
    Accounts for
    (i) ratio of pupil area to retinal area
    (ii) spectrometer coverage of monitor
2021-10-10 add mosfet plus voltage regulator link
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2022-01-26 add initial sketch of ND filter holder
    [ND_filterholder.scad]
2022-02-28 update nd filter holder
    [ND_filter_socks.3mf, ND_filterholder.3mf, ND_filterholder.scad, filter_hanger.3mf]
2022-03-09 update LCR-addon board
    - solve mounting holes
    - solve alignment target on the user layer
    - check connections
    [Lcr_addon-B_Adhes.gbr, Lcr_addon-B_CrtYd.gbr, Lcr_addon-B_Cu.gbr, Lcr_addon-B_Fab.gbr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]
2022-03-13 adjust filter holder pocket
    [ND_filterholder.scad, ND_filterholder_large_filter.3mf]
2022-05-16 update sock holder
    [ND_filterholder.scad, ND_filterholder_5mm_thick_filter.3mf, ND_filterholder_large_filter.3mf, light guide holder.3mf]
2022-10-13 add models for filter holder
    [ND_filterholder.scad, ND_filterholder_5mm_thick_filter.3mf]
2023-12-06 update nd filter holder and remove board backups
    [ND_filterholder_rigid_plastic.scad, ND_filterholder_rigid_plastic.stl]

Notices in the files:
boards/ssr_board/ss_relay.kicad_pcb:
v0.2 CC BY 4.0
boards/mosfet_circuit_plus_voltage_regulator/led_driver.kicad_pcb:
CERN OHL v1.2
